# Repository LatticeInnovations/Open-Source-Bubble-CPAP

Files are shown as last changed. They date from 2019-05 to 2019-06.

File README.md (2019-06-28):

# Open-Source-Bubble-CPAP
This is an open source Bubble CPAP project
# This document is the chronological archive of the open bubble CPAP Design. It shows the working principle of the CPAP system

> ## [Iteration 1:](https://github.com/LatticeInnovations/Open-Source-Bubble-CPAP/tree/master/01.%20Base%20Design/Iteration%201) 

>> This is the first proposed design. It includes industrial grade as well as readily available off-the-shelf materials. 

>>[It consists of the basic fundamental parts of the system. I.e.](https://github.com/LatticeInnovations/Open-Source-Bubble-CPAP/tree/master/03.%20Materials%20and%20testing/iteration%201/BOM-rev01) 

>> - Air compressor
>> - Flow meter
>> - Humidifier
>> - PEEP bottle
>> - Nasal prong

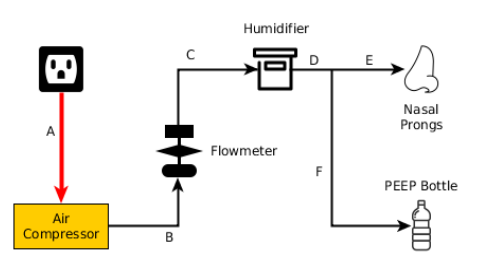
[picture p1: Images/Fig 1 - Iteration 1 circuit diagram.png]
Fig 1: Iteration 1 breathing circuit
>>> 

> ## [Iteration 2: ](https://github.com/LatticeInnovations/Open-Source-Bubble-CPAP/tree/master/01.%20Base%20Design/Iteration%202) 

>> Tests, observations and changes:

>> - Air compressor, alternative enclosure and hardware selection.
>> - [Breathing circuit pressure validation:](https://github.com/LatticeInnovations/Open-Source-Bubble-CPAP/blob/master/03.%20Materials%20and%20testing/iteration%202/Bubble%20VS%20Surface%20Humidifier%20Data/(S.H%20vs%20B.H)%201-of-2%20PEEP%20pressure%20validation%2026-06-2018.pdf) Relation between PEEP submersion depth (cm), Flow rate(Lpm) and pressure (manometer reading)
>> - Pressure deviations between bubbling & non-bubbling humidifiers.
>> - Water filling and submersion depth control.

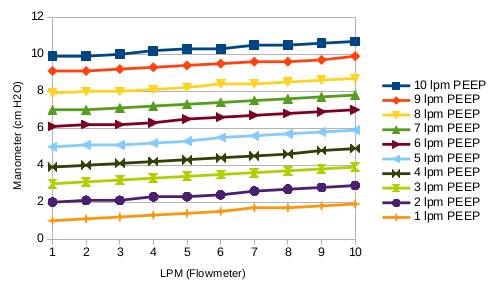
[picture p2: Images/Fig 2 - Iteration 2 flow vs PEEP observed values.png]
Figure 2: Iteration 2 - Flow vs PEEP observed values
>>> 

>> ### [Iteration 2.0](https://github.com/LatticeInnovations/Open-Source-Bubble-CPAP/tree/master/03.%20Materials%20and%20testing/iteration%202/iteration%202.0) 

>>> Gas detection (NH4, CO, CO2, Propane etc.) to identify the reason of smell inside the breathing circuit. 
>>> Effect on humidity with variable surface area inside the humidifier to control humidification.

>> ### [Iteration 2.1](https://github.com/LatticeInnovations/Open-Source-Bubble-CPAP/tree/master/03.%20Materials%20and%20testing/iteration%202/iteration%202.1) 

>>> Breathing circuit leakage detection technique and results

>> ### [Iteration 2.2](https://github.com/LatticeInnovations/Open-Source-Bubble-CPAP/tree/master/03.%20Materials%20and%20testing/iteration%202/iteration%202.2) 

>>> Load testing for 3 days & observations on stability of the in-circuit humidification irrespective of ambient temperature & humidity >>> change.

> ## [Iteration 3:](https://github.com/LatticeInnovations/Open-Source-Bubble-CPAP/tree/master/03.%20Materials%20and%20testing/iteration%203) 

>> - Comparison with Pumani and experiments on rebreathing of CO2 in Open bubble CPAP.
>> - Humidifier water filling mechanism with ball valve.
>> - Load testing with the new humidifier setup, continuous run for more than 8 hours
>> - Comparison between looped vs unidirectional (separate inspiratory & expiratory limb) nasal prongs usage

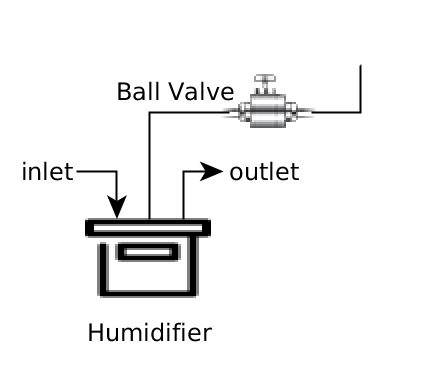
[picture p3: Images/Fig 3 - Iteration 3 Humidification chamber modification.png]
Figure 3: Iteration 3 - Humidification chamber modification
>>> 

> ## [Iteration 4:](https://github.com/LatticeInnovations/Open-Source-Bubble-CPAP/tree/master/03.%20Materials%20and%20testing/iteration%204) 

>> - Humidifier selection revised. Medical grade commonly available bottle shaped humidifiers. 
>> - Alternate silicone tubing for the breathing circuit. (ID-8mm, OD-12 mm)
>> - It has advantage of compatibility with a wide range of tube connectors.
>> - Oxygen blending feature addition in CPAP.
>> - 3-Flow-Meter method in contrast with existing pumani 2 FM design.
>> - Oxygen cylinder valve comparison and operating pressure levels selection.

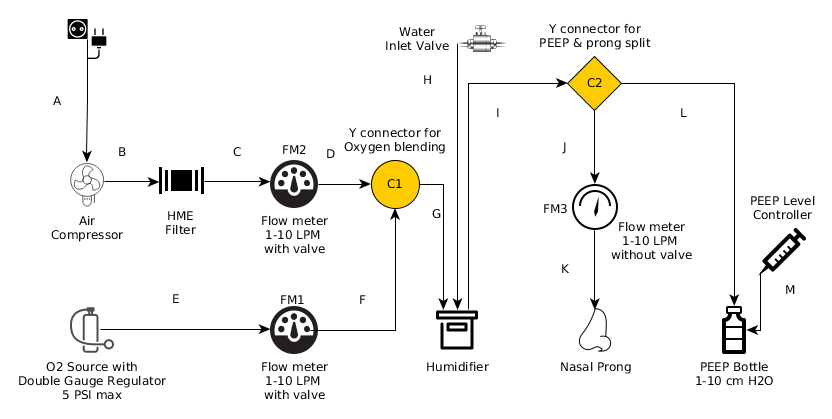
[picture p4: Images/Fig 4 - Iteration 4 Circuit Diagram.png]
Figure 4: Iteration 4 - Iteration 4 - Breathing Circuit
>>> 
***
## Development of OpenSource and affordable bubble CPAP system for neonatal respiratory care

.
#### Introduction:

Preterm infants commonly suffer from a respiratory/breathing disorder called neonatal respiratory distress syndrome (RDS) as their lungs are not yet fully developed. The disease is mainly caused by a lack of a slippery substance in the lungs called surfactant that helps the lungs fill with air and keeps the air sacs from deflating. The surfactant is present when the lungs are fully developed. Neonates suffering from RDS often need breathing support until their lungs start making enough surfactant. 

Continuous positive airway pressure (CPAP) as a therapy for respiratory distress syndrome, is the application of positive pressure to the airways of spontaneously breathing neonates throughout their respiratory cycle.

#### Aim:

Conventional CPAP is very expensive and hence not affordable in resource-constrained settings. Locally available hardware such as low-cost plastic bottles, tubing, connectors and air pumps are used in this design to develop an affordable and modular Bubble CPAP device. With the modular CPAP approach, we intend to locally train more people on how to develop and troubleshoot CPAP devices. 

#### Purpose of usage:
- Maintaining both breathing parameters i.e. the volume and the pressure of the inhaled gas to the lungs in order to prevent lung collapse among RDS affected neonates/patients.
- To make sure that the prescribed level of oxygen is supplied to the patient through the air/O2 mixture so that it can take part in the gas exchange process in the alveoli.
- Helping the patient breath by reducing the work of breathing.

### How to use this document: 

This opensource DIY design of this bubble CPAP is module driven. The entire design is divided into three segments: 

**1. [Base Design](https://github.com/biplabro/Open-Source-Bubble-CPAP/tree/master/01.%20Base%20Design) :**
This is the bare minimum design of the Bubble CPAP system and it represents the updated design guidelines of the latest design iterations.

**2. [Optional Add-ons](https://github.com/biplabro/Open-Source-Bubble-CPAP/tree/master/02.%20Optional%20Add-ons) :**
This section of the document includes all the additional hardware 

**3. [Material Specifications & Testing Protocols](https://github.com/biplabro/Open-Source-Bubble-CPAP/tree/master/03.%20Materials%20and%20testing) :**
In this section, hardware materials, test procedures and outputs are discussed. 

**The idea of the development process is:**
- To build a working CPAP device using the most commonly used & readily available resources.
- To shrink the base design while retaining the robustness, reliability and functionality of the system so that it can be used as a standalone bare minimum design.
- To include more resources, features and test cases in the Optional Add-ons & Testing protocols segments so that it can be further developed with different design approaches.

#### Features and specifications:

* Flow rate: 1 to 10 lpm
* PEEP: equivalent to 1 to 10 cm of water column
* Power input: 220v, 50Hz (inpun is air compressor dependant and entirely flexible)
* HME filtration (optional) for particulate free clean air.
* Both valve regulated or disposable humidifier can be used for easy access
* 3-flowmeter design for better air-oxygen blending and control of the total flow. 
* Can be built from scratch & easily accessible off-the-shelf components based desig.
* Max pressure for O2 cylinder interface: 5 PSI

**How to build:**

The [“01. Base Design”](https://github.com/biplabro/Open-Source-Bubble-CPAP/tree/master/01.%20Base%20Design)  folder includes all the building iterations. [“Iteration 5”](https://github.com/biplabro/Open-Source-Bubble-CPAP/tree/master/01.%20Base%20Design/Iteration%205)  (or the largest number) sub-folder includes the latest build instructions with pictures. 

Size and outlook of the built devices across the globe may differ depending on the availability of the components/ alternative components.

[**Base Design:**](https://github.com/LatticeInnovations/Open-Source-Bubble-CPAP/tree/master/01.%20Base%20Design) 

1. Base device is intended to be treated as a self sufficient working model of the bubble CPAP system. 

2. BOM, available datasheets etc. are included in the “03. Material and testing” folder. We have to keep in mind that the generic components like silicone tubing, HME filters etc. can come from different local and global manufacturers. Every iteration done by the users must include the actual images to help others source the desired item.

3. The basic working principle of respiratory support system like bubble CPAP is to provide the patient with air and gas supply with controlled Volume & Pressure to prevent their lung from collapsing. The flow-meters deployed in the breathing circuit takes care of the volume of the exhausted air/oxygen mixture from the device and the water submersion leven inside the PEEP determines the exerted pressure level to the patient’s lungs. 

4. In the last iteration air. Oxygen is blended through a Y-connector piece with regulated flow and pressure. A table of O2/Air mixture concentration is included in the “03. Material and testing” folder for reference. 
 5. Every tube-connector junction is to be fixed properly to assure no leakage within the breathing circuit.
 
[**Optional Add-ons:**](https://github.com/LatticeInnovations/Open-Source-Bubble-CPAP/tree/master/02.%20Optional%20Add-ons)

1. Optional add-ons can or cannot be implemented with the base design. It entirely depends on the access & availability of the additional components. 

2. HME filters, Valve regulated water filling technique etc. should be considered as extra that does not have a significant direct impact on the usability of the base device. 

3. Users are encouraged to include additional hardware to their respective system to make it more robust & reliable.

[**Materials & Testing Protocols:**](https://github.com/LatticeInnovations/Open-Source-Bubble-CPAP/tree/master/03.%20Materials%20and%20testing) 

This folder includes the following :
- all the testing protocol and experiment data, 
- Software codes required for conducting the experiments. 
- Bill of materials and observations on 
	    1. O2 concentrator
   	2. Flow meter etc
  	3. comparison on different nasal prongs
  	4. Filters
 	5. Pressure levels for interfacing external oxygen cylnder
 	
 Enlisting all the tests conducted from phase 1 to phase 3 and how the development is iterated based on the test results

**Other:**
Tubing of the breathing circuit is preferred to be of same internal dia, it will assure more accurate readings with the flow-meter.

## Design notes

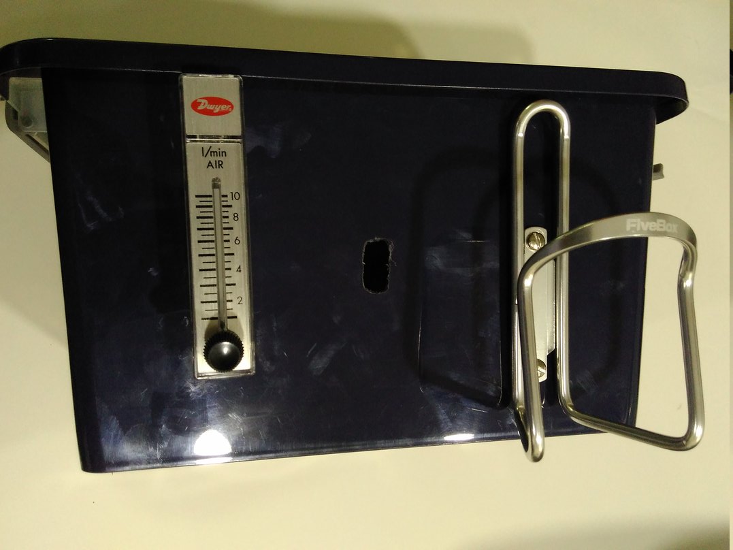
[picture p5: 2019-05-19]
01. Base Design/Iteration 1/Design files/Images_rev01/rev01-19.jpg

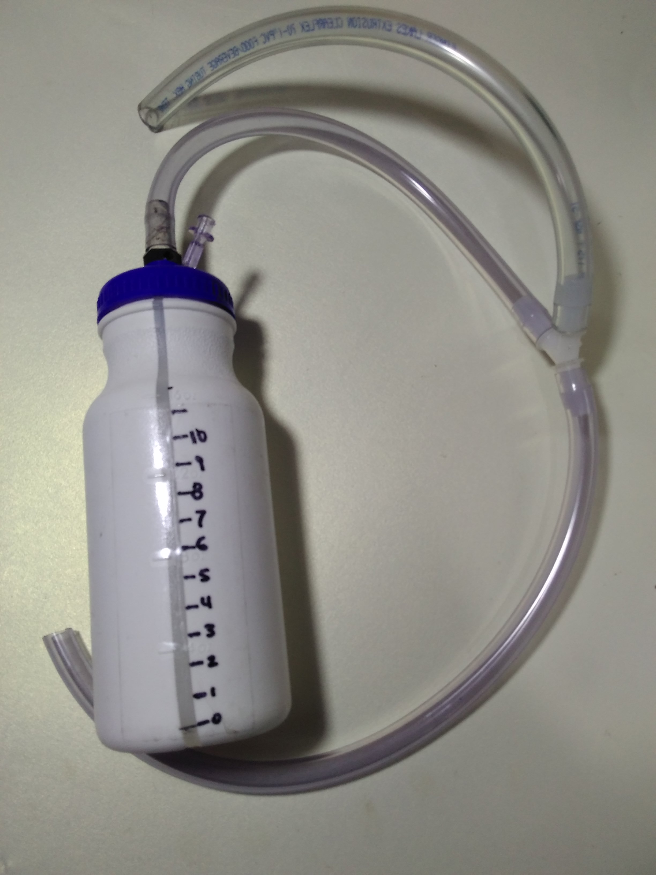
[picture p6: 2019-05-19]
01. Base Design/Iteration 1/Design files/Images_rev02___rev03/rev02-23.jpg

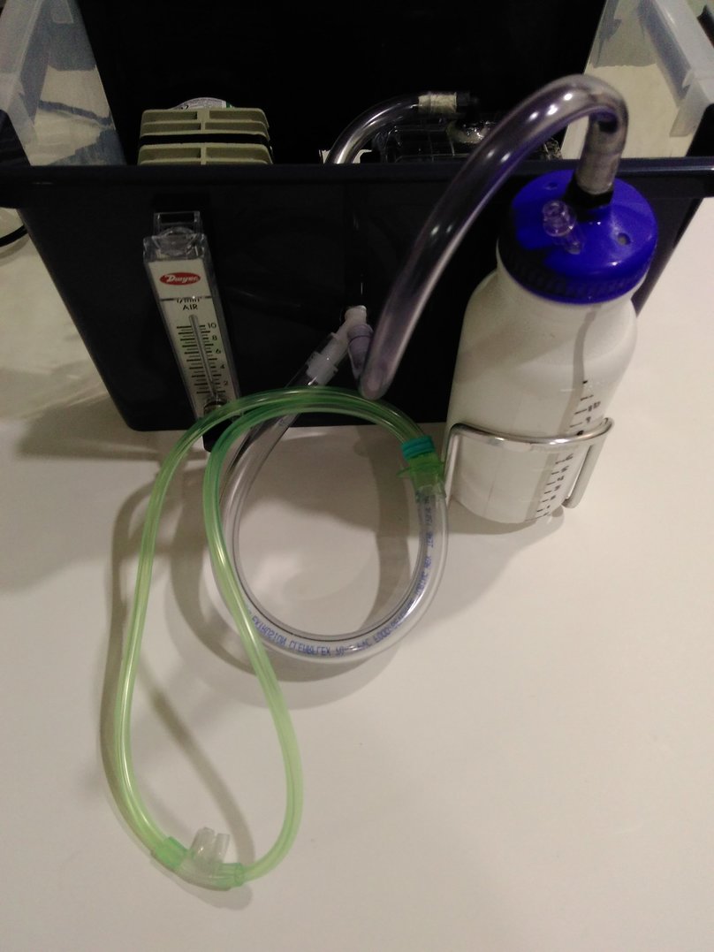
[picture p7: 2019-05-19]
01. Base Design/Iteration 1/Design files/Images_rev01/rev01-27.jpg

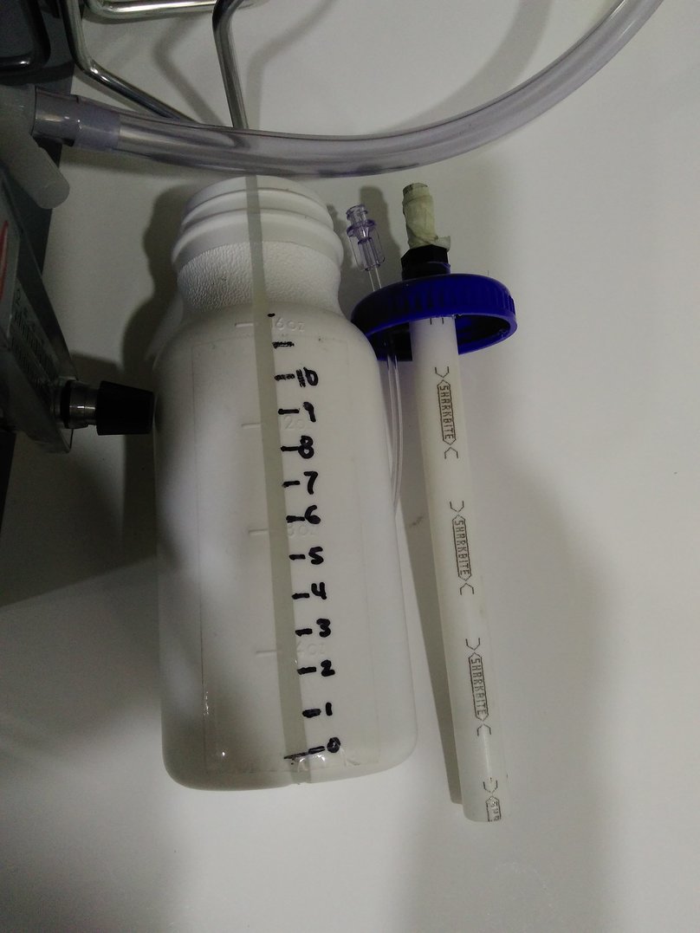
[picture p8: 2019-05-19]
01. Base Design/Iteration 1/Design files/Images_rev01/rev01-25.jpg

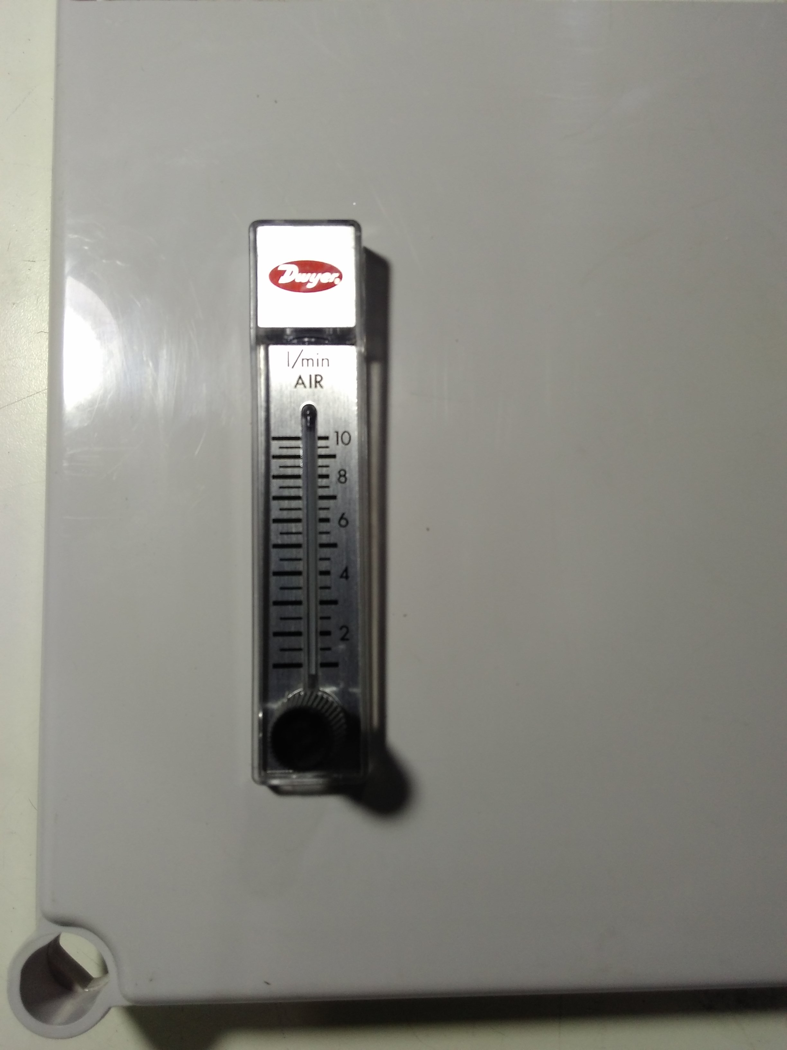
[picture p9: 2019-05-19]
01. Base Design/Iteration 1/Design files/Images_rev02___rev03/rev02-17.jpg

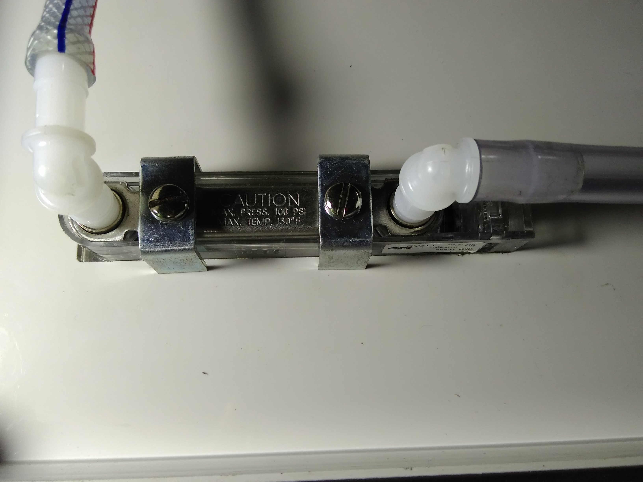
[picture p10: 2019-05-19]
01. Base Design/Iteration 1/Design files/Images_rev02___rev03/rev02-20.jpg

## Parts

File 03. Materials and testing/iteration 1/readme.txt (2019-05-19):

Readme: Low-cost Bubble CPAP device development. This folder contains all the test protocol, results, data & plots.

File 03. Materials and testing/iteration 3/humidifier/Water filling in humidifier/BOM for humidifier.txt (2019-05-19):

1. Forged ball valve 1/2" 
2. Nozzle for ball valve 1/2" to 3/8"
3. Tube fasteners 3/4"
4. Teflon tape
5. U clamp 1" dia, 3/4" width
6. Funnel for pouring water (optional)

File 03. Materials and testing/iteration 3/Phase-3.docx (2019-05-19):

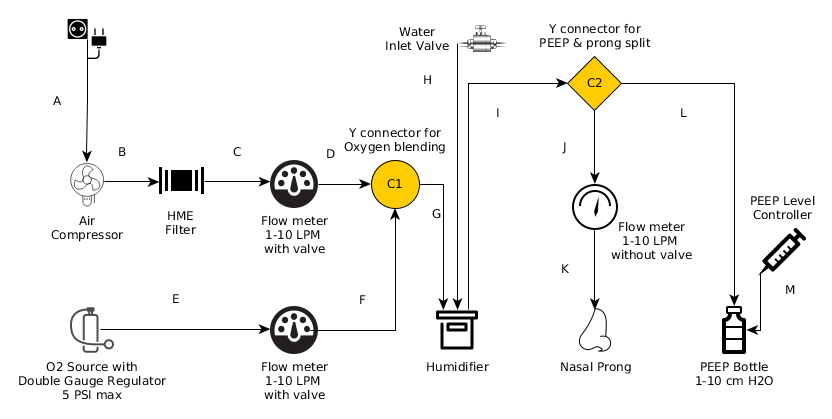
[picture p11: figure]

Water Inlet Valve

Y connector for PEEP & prong split

C2

Y connector for Oxygen blending

сі

PEEP Level Controller

Air Compressor

HME Filter

Flow meter

1-10 LPM with valve

Flow meter

1-10 LPM without valve

>6

Humidifier

Nasal Prong

02 Source with Double Gauge Regulator

5 PSI max

Flow meter

1-10 LPM with valve

PEEP Bottle 1-10 cm H2O

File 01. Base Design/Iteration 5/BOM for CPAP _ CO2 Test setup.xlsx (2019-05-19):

 | All materials are referenced to the attached system schematic diagram
 |  |  |  |  |  |  | Legends:
 |  |  |  |  |  |  | Optional Item
Sl. No. | Component Type | Count | As shown in Diagram | Vendor | Manufacturer Part No. | Description | Datasheet | product link | link for purchase
1 | Air compressor | 1 no. | Air compressor | Amazon India | ACO-308 | Hailea Air Compressor ACO-308, 22W. 220V/50Hz; 45LpM | http://www.aeroponic.gr/en/eshop/hailea-aco-308-detail.pdf?tmpl=component | http://www.hailea.com/e-hailea/product3/ACO-308.htm | http://www.amazon.in/HAILEA-ACO-308-Hailea-Air-Compressor/dp/B0083UFKDG
2 | L connector for Flowmeter | 4 nos. | C-FM2-D, E-FM1-F, M-FM3-N | McMASTER-CAR | 2808K121 | Polyethylene Barbed Tube Fitting 90 Degree for 3/8“ Elbow Tube | https://www.mcmaster.com/#2808k121/=189an7w | https://www.mcmaster.com/#2808k121/=189an7w | https://www.mcmaster.com/#2808k121/=189an7w
3 | HME filter Disk type | 1 no. |  |  |  |  |  | http://mederen.com/uploads/catalogue/respiratory_and_anestesia/heats/thumbnail/h2-f1000x1000.jpg | https://www.larsmedicare.com/hme-filter/
4 | Flow meter 1-10 LPM | 3 nos. | FM1, FM2, FM3 | Amazon | homyl | Homyl 1-10LPM Tube Type Oxygen Flow Meter Flowmeter Regulator With Valve,Measuring And Controlling Air |  | https://www.amazon.in/gp/product/B07HSKD591/ref=oh_aui_search_detailpage?ie=UTF8&psc=1
5 | End cap for fitting HME filter with tube | 2 nos.
6 | alternative HME filter (no extra end cap required, replacement for tem no. 5 & 6) | 1 no. |  |  |  |  |  | https://scientificfilters.com/store/filtration-devices-syringe-filter-rezist-10463607
7 | Straight connector with threading | 3 nos. | G-Humidifier-H-I | McMASTER-CAR | 2429k16 | Plastic Barbed Tube Fitting for Air and Water | https://www.mcmaster.com/2429k16 | https://www.mcmaster.com/2429k16 | https://www.mcmaster.com/2429k16
8 | Tubing for breathing circuit | 7 mtr. | A,B,C,D,E,F,G,H,I,J,K,L,M,N | Generic |  | Tube ID: 8mm, OD: 12mm, soft silicone, Lab equipment grade, autoclavable |  | https://www.alibaba.com/showroom/silicone-tube-for-laboratory.html
9 | Humidifier chamber | 1 no. | Humidifier | Roxx |  | small Plastic Waterproof Airtight Case |  | https://www.amazon.in/gp/product/B007PDU6IQ/ref=oh_aui_search_detailpage?ie=UTF8&psc=1
10 | alternative disposable humidifier chamber | 1 no. |  | Generic |  | Medical grade humidifier |  | https://www.4mdmedical.com/disposable-humidifier-6-psi.html
11 | Y connector (1 for CO2 testing) | 2 +1 nos. | C1, C2, C3 | McMASTER-CAR | 2808K131 | Plastic Wye Connector, for 3/8" Tube ID | https://www.mcmaster.com/#2808k131/=189hu45 | https://www.mcmaster.com/#2808k131/=189hu45 | https://www.mcmaster.com/#2808k131/=189hu45
12 | Ram cannula | 1 no. | Nasal Prong | http://pro-med.cn | P2001001, P2001002, P2001003, P2001004 | Nasal Oxygen Cannula |  | http://pro-med.cn/PRODUCTS/RespiratoryRanges/340484.shtml | http://pro-med.cn/PRODUCTS/RespiratoryRanges/340484.shtml
13 | PEEP bottle | 1 no. | PEEP bottle | Quechua |  |  |  | http://www.amazon.in/Quechua-Hiking-Bottle-Cutlery-Yellow/dp/B00HZETOS8 | http://www.amazon.in/Quechua-Hiking-Bottle-Cutlery-Yellow/dp/B00HZETOS8
14 | Adjustable Bottle holder | 1 no. | PEEP bottle | Generic |  | Bottle Carrier Bracket |  | http://www.amazon.in/Arrival-Adjustable-Plastic-Cycling-Accessories/dp/B01MG1YRLG | http://www.amazon.in/Arrival-Adjustable-Plastic-Cycling-Accessories/dp/B01MG1YRLG
15 | PVC tube inside PEEP Bottle | 6" | PEEP bottle | Generic |  | OD: 16mm ; ID: 12mm
16 | Sytinge for PEEP level control | 1 no. | PEEP level controller |  |  |  |  |  | https://www.amazon.in/SaiDeng-Reusable-Syringes-Cleaning-Measuring/dp/B07Q12KHPD?s=kitchen
17 | CPAP enclosure | 1 no. |  | Rolec India | BC-AGS -283818 | Enclosure for CPAP device |  | http://www.rolecenclosures.in/
18 | Forged ball valve 1/2" | 1 no. | Water inlet valve |  |  |  |  | images attached in the folder
19 | Nozzle for ball valve 1/2" to 3/8" | 2 nos. | Water inlet valve
20 | Tube fasteners 3/4" | 2 nos. | Water inlet valve
21 | Teflon tape | 1 nos. | Water inlet valve
22 | U clamp 1" dia, 3/4" width | 2 nos.
23 | Funnel for pouring water (optional) | 1 nos.
24 | Oxygen cylinder regulator | 1 nos. | O2 Source Regulator |  |  | Dual gauge single stage valve regulator |  | https://www.amazon.in/Bloomerang-Welding-Victor-Cutting-Regulator/dp/B07JM6RMK4
25 | CO2 testing enclosure | 1 No. |  |  |  | Bottles similar to this |  | https://www.amazon.in/Cello-Unbreakable-Plastic-Bottle-Litre/dp/B01BYBTZJA?s=kitchen
26 | MQ-135 CO2 sensor | 2 nos. | Sensor |  |  |  | https://www.olimex.com/Products/Components/Sensors/Gas/SNS-MQ135/resources/SNS-MQ135.pdf | https://www.amazon.in/REES52-Arduino-Compatible-Sensor-Methane/dp/B018GW70G0?s=gateway
27 | Arduino UNO with USB cable | 1 no. | Data logging Module |  |  |  | https://www.farnell.com/datasheets/1682209.pdf | https://www.amazon.in/Uno-ATmega328P-Compatible-ATMEGA16U2-Arduino/dp/B015C7SC5U?s=gateway

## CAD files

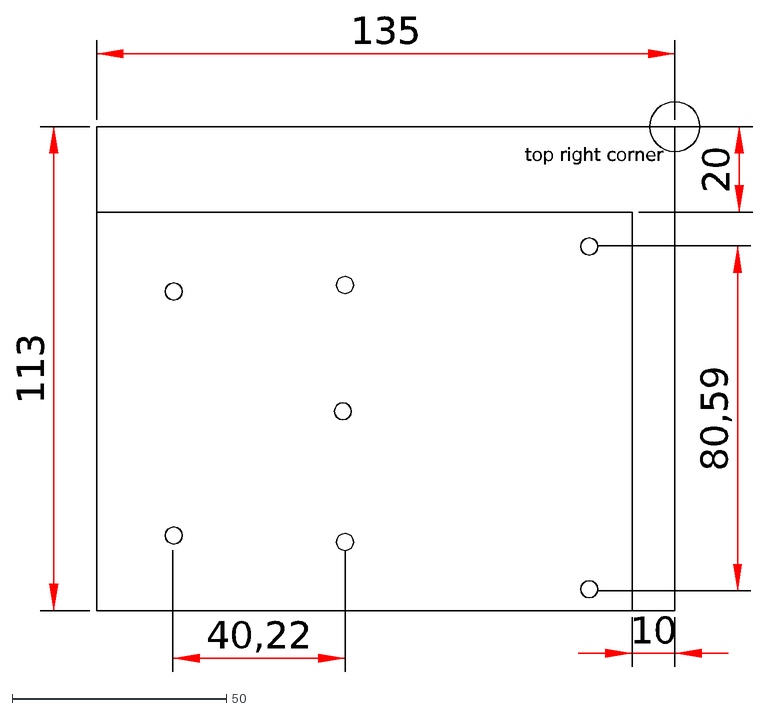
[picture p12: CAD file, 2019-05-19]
01. Base Design/Iteration 1/Design files/CPAP_Baseplate_file.dxf
10
20
113
135
top right corner
40,22
80,59

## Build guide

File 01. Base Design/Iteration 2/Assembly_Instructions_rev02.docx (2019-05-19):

Assembly instruction for CPAP device

Step 1.1 Prepare the cut outs in the main enclosure

Step | Instruction | Image

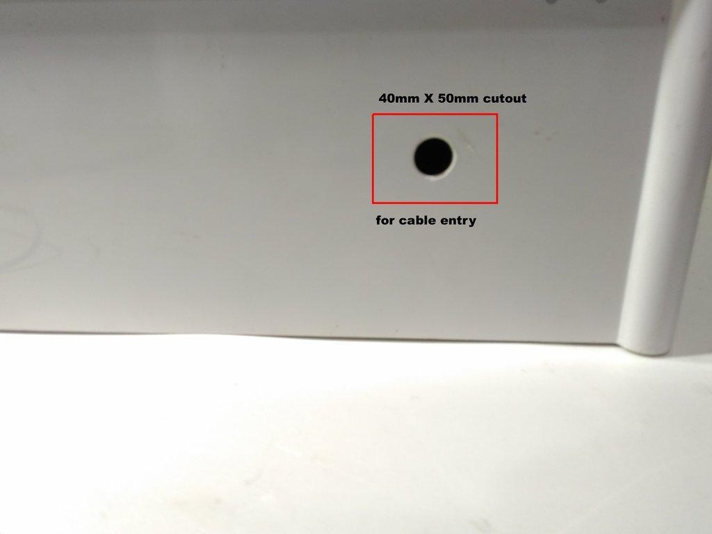
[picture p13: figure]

1.0 | Make a 40mm X 50mm clearance for cable inlet at any of the side walls of the enclosure. | Fig.0

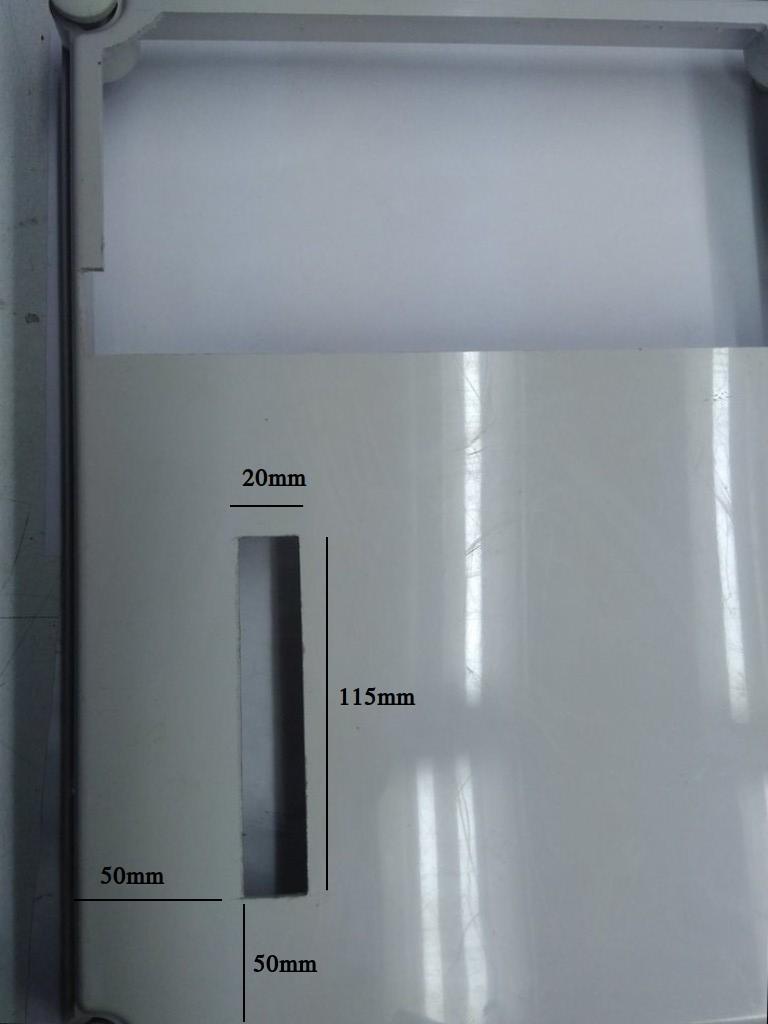
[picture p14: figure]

| Note the location of the flowmeter installation cavity. | Fig.1

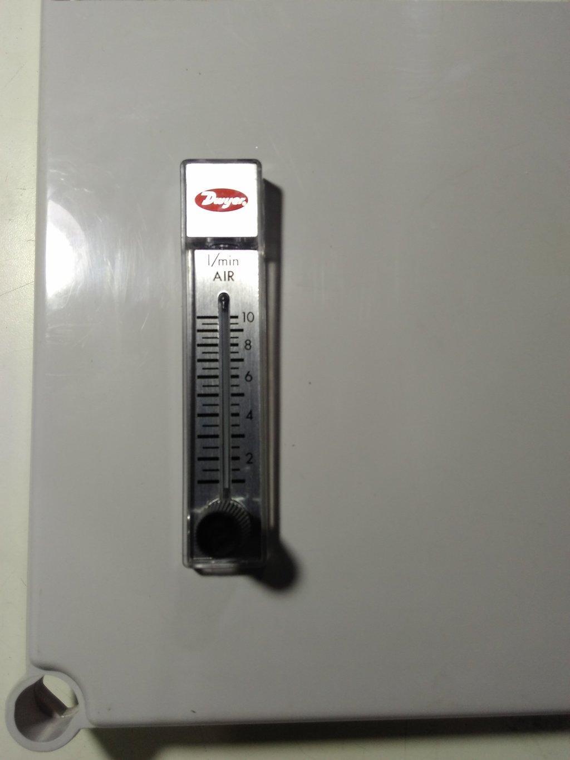
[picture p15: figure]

1.2 | Place it as shown | Fig.2

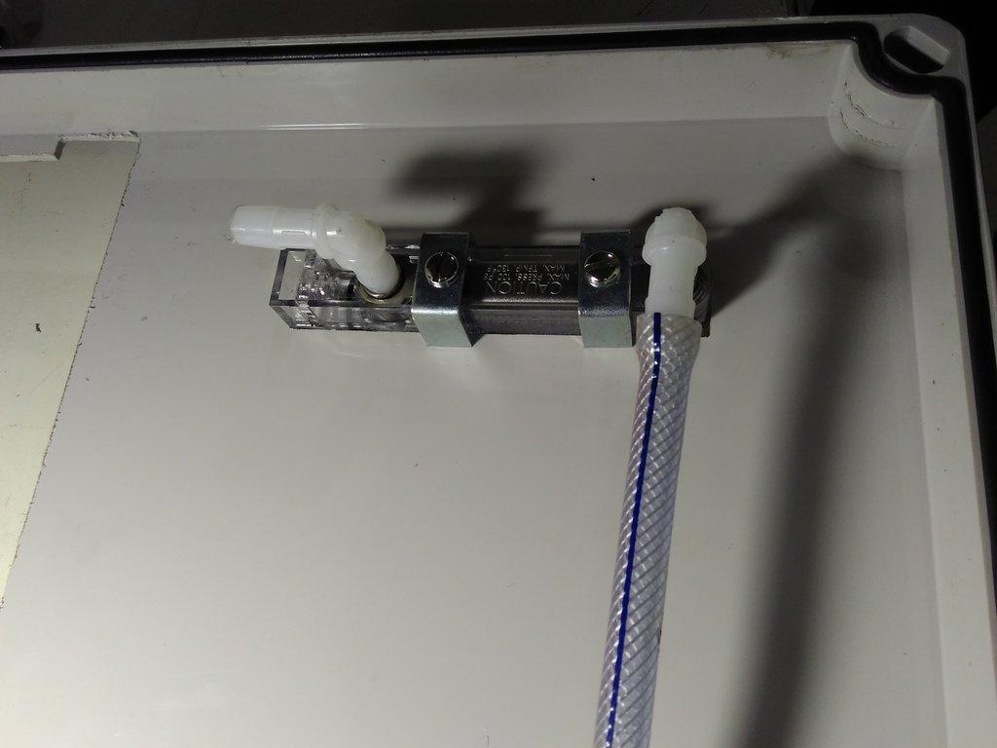
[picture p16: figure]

1.3 | Fix the screws to keep the flowmeter in place. | Fig.3

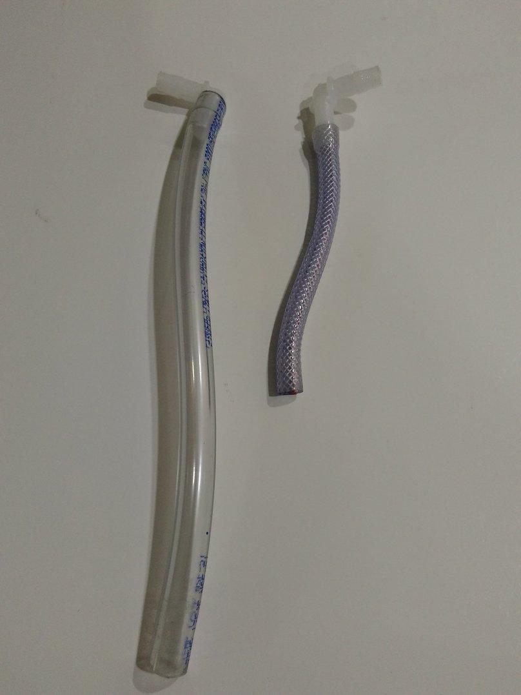
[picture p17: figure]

1.4 | Cut two PVC tubes of 250mm & 120mm length & connect the elbow connectors to the tubes as shown in the picture. | Fig.4

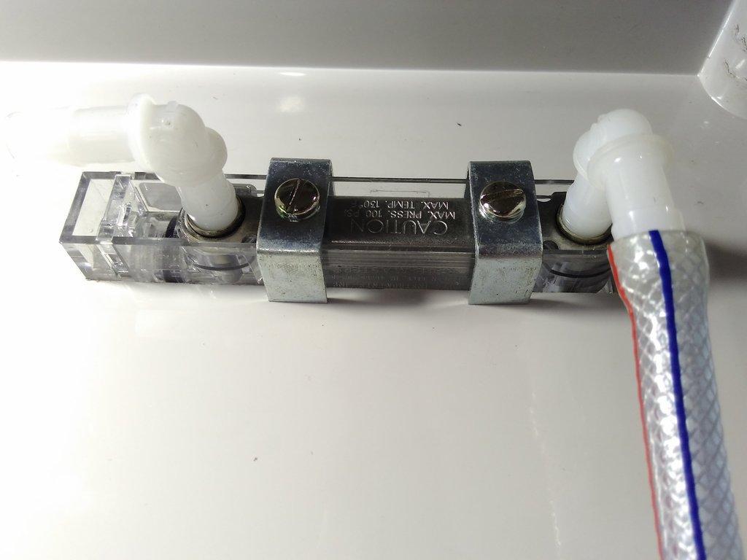
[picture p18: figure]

1.5 | Connect the tubes to the flowmeter. There are no threads built in to the plastic connectors, tighten the elbow connectors carefully & the metal threads will automatically cut the plastic & make an airtight threading. | Fig.5

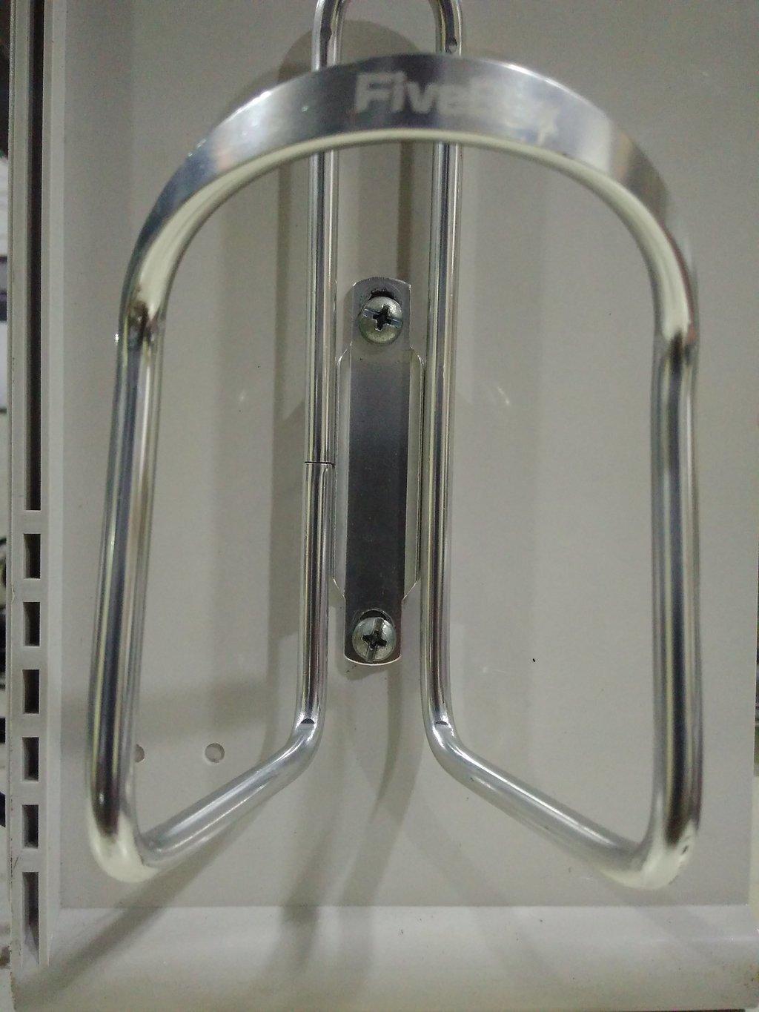
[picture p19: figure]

1.6 | Drill two holes of 5mm dia & 65mm apart and fix the bottle holder in that location. | Fig.6

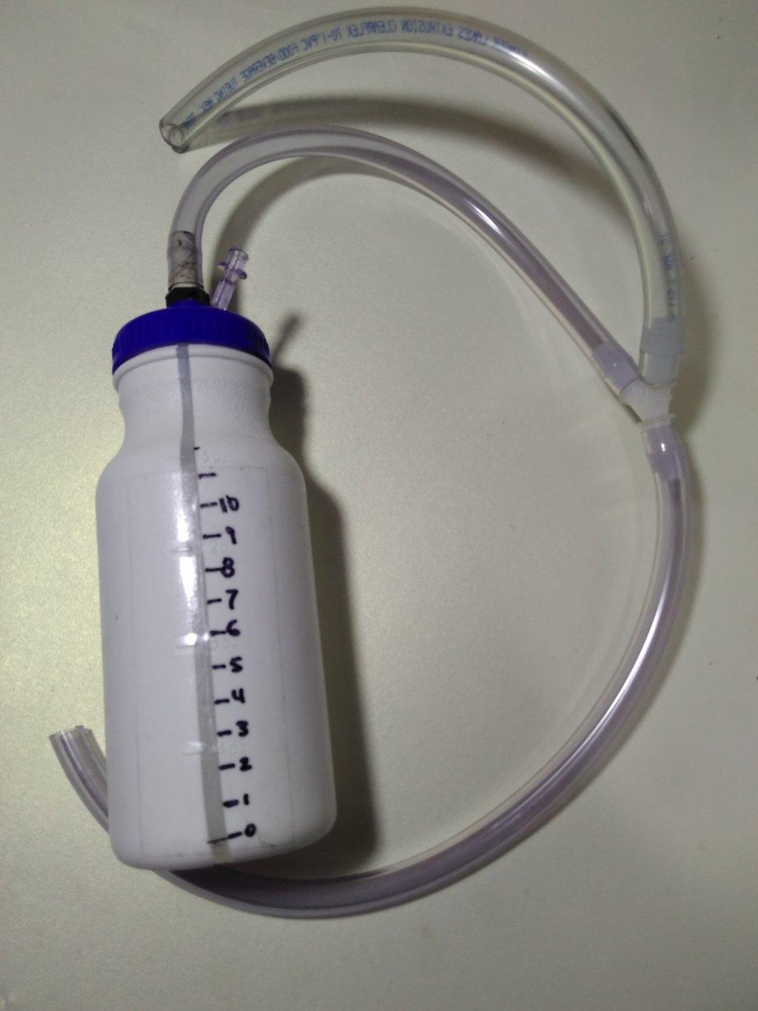
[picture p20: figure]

1.7 | Prepare the PEEP bottle assembly | Fig.7

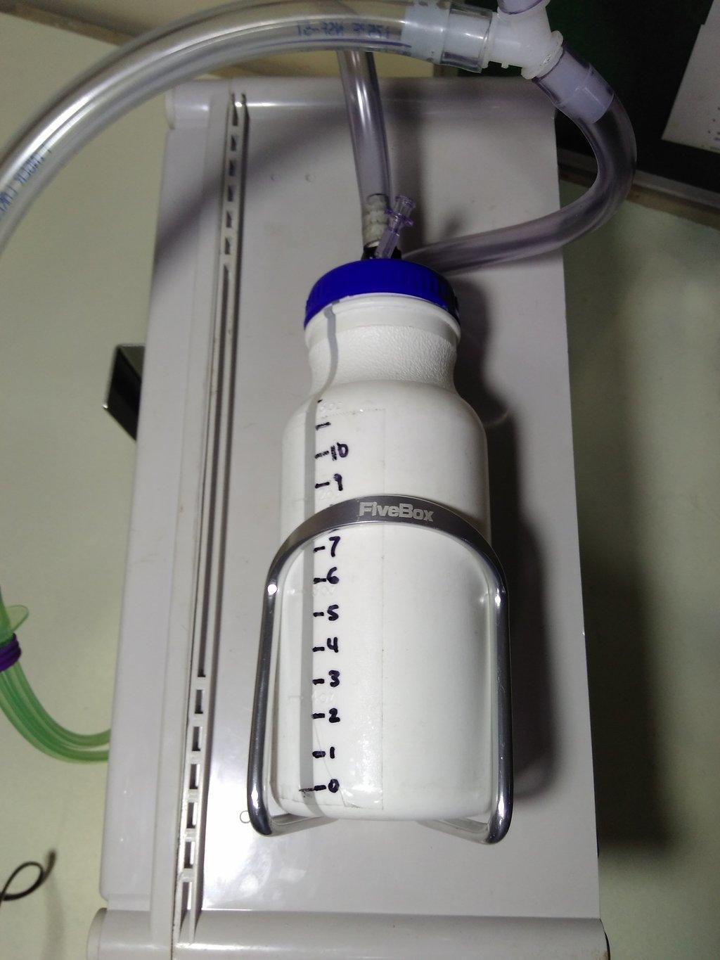
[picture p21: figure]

| PEEP bottle to be mounted as shown. | Fig.8

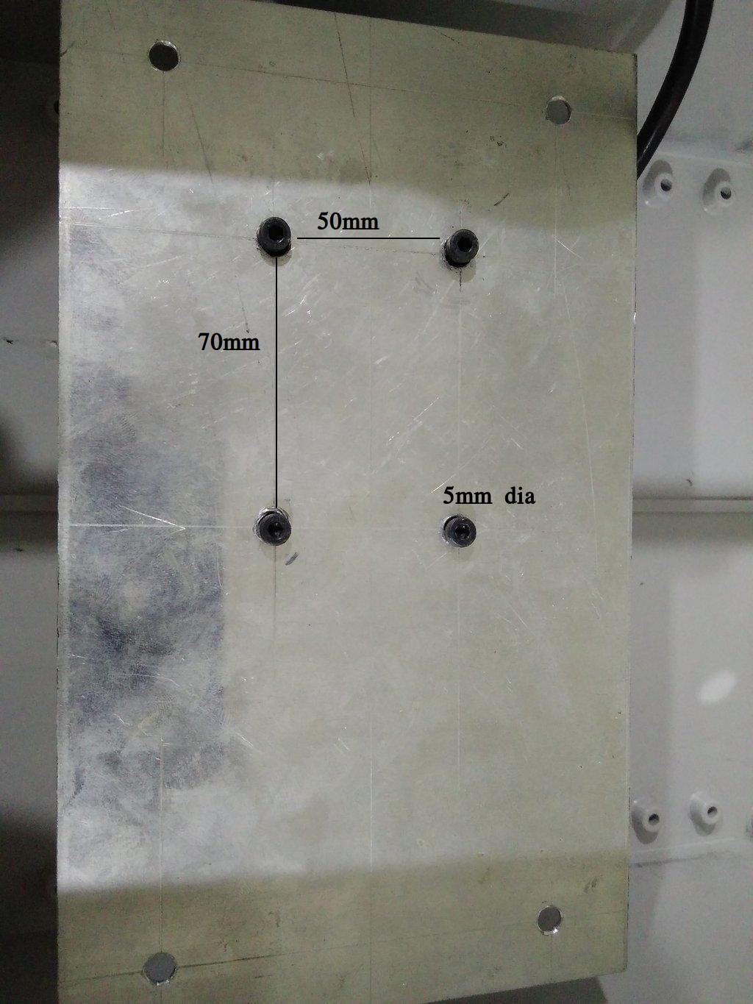
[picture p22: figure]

| Prepare the base-plate for compressor mounting. Placement of the holes may differ depending on their actual mounting arrangement | Fig.9

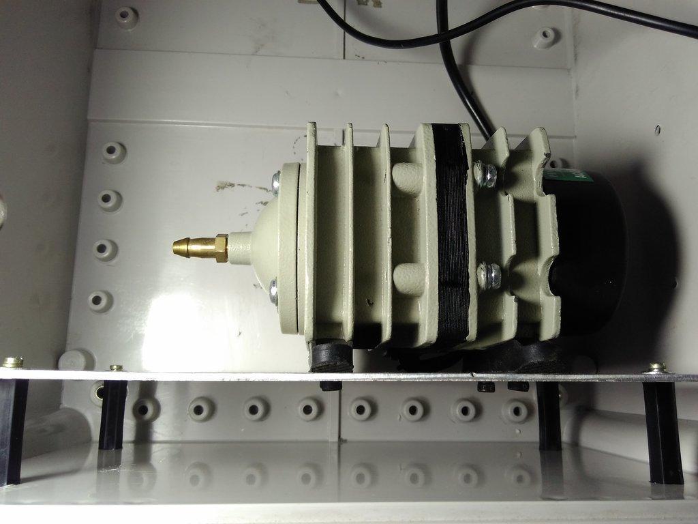
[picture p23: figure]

1.8 | Assemble the pump & place it in the mounting holes. Make 4 mounting holes for placing the baseplate inside the enclosure. Dimension: 190mm X 90mm | Fig.10

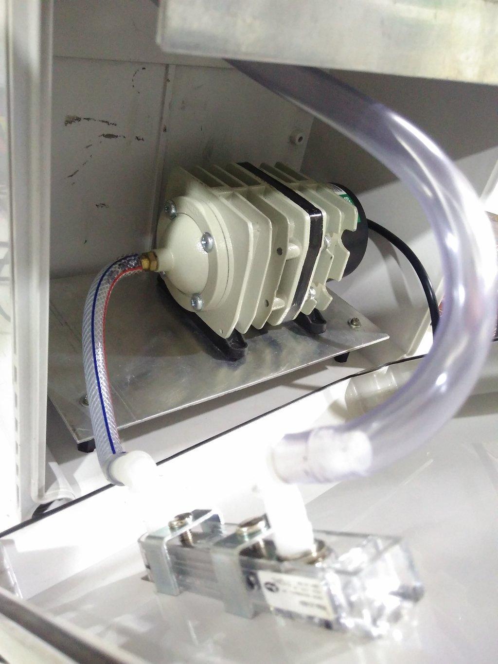
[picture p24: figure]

| Connect the compressor outlet to the flowmeter inlet as shown. The outlet of the flowmeter to be connected to the inlet of the humidifier. | Fig.11

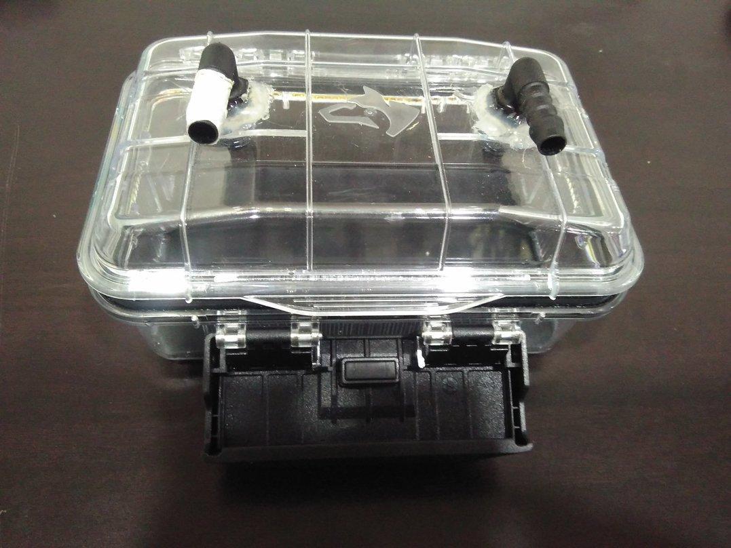
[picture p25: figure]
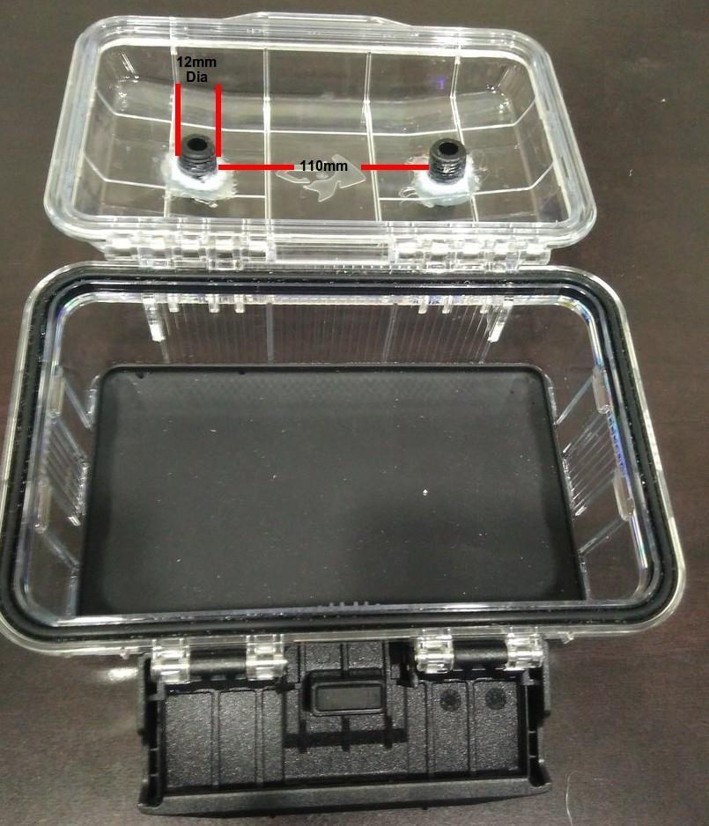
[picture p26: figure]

1.9 | Preparation of the Humidifier Drill two holes of 12mm dia & 110mm apart and place the threaded elbow connector as shown in the image. Some masking tape can be applied for achieving better grip & air-tightness. | Fig.12 Fig.13

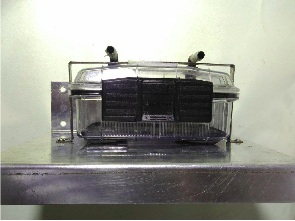
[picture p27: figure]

1.10 | Place the humidifier chamber in the appropriate place. | Fig.14

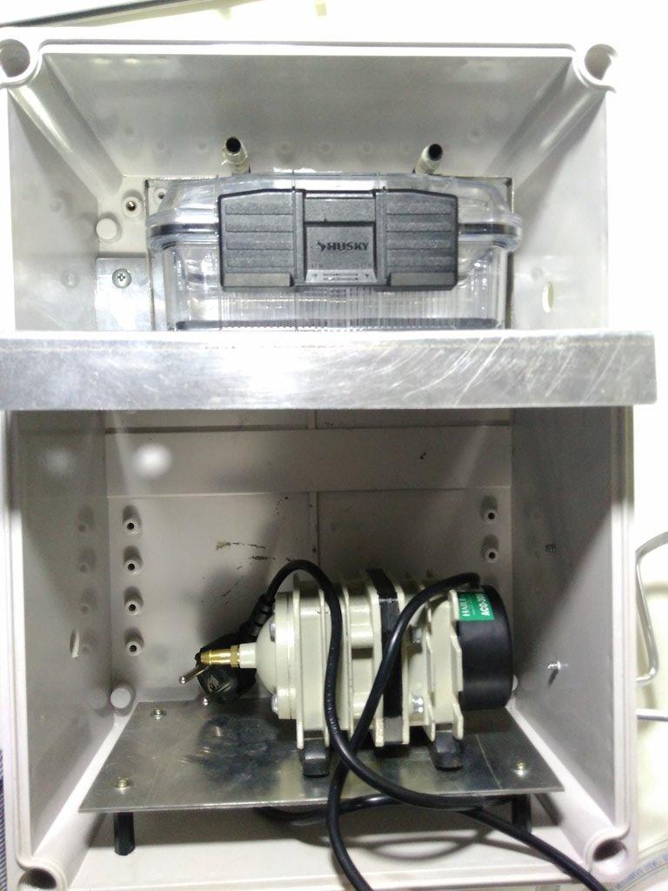
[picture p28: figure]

1.11 | The final placement of compressor & humidifier | Fig.15

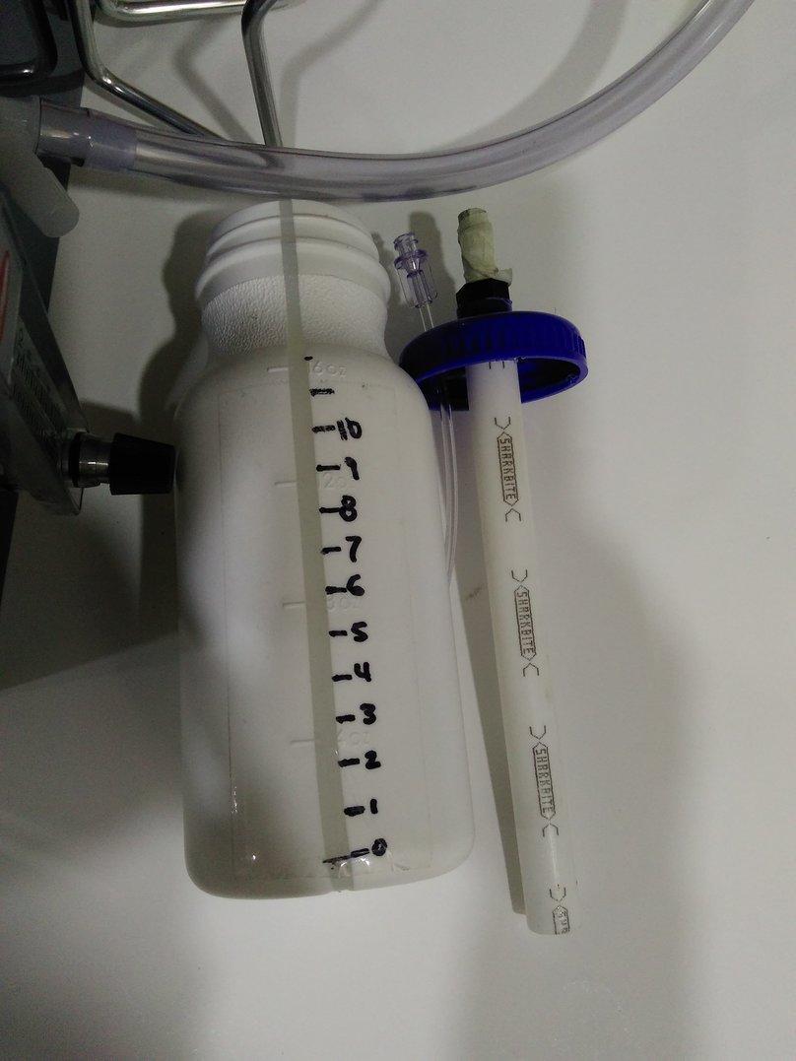
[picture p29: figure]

1.12 | Drill a hole of 12mm diameter at the center of the cap of the bottle & place the threaded connector & 180mm PVC pipe of 12mm internal diameter. Drill 4 holes of 5mm diameter at the cap of the bottle to insert luer lock tubing. This tube will be connected to a 60ml or 100ml syringe for adding or reducing water to the PEEP bottle. | Fig.16
1.13 | Cut a 115mm tube & place it in between the humidifier chamber outlet & Y connector. Connect the nasal cannula & tubing to the wye connector. | Fig.17

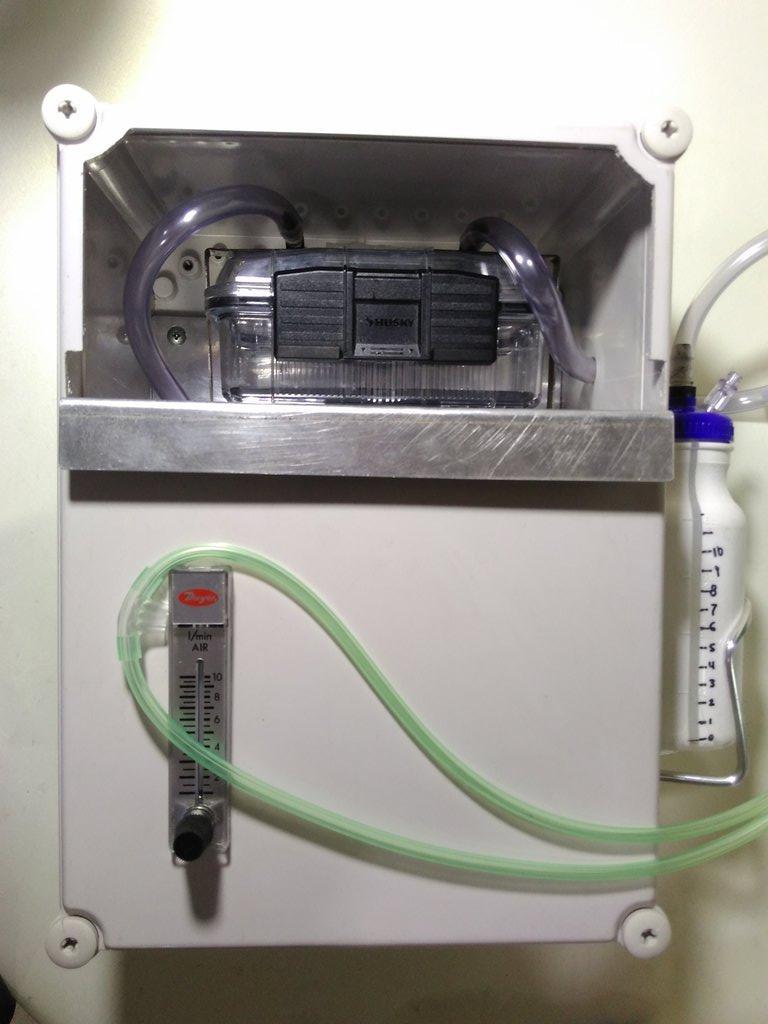
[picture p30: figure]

1.14 | Assembled bubble CPAP | Fig.18

For Internal use only Lattice Innovations FYVE S1 SOP Assembly Instructions Document No – LI/QM/SOP/AI/CPAP Version No. 02 New ___ _________ Revised ___________ Effective Date: Issuing Date: 17-07-201

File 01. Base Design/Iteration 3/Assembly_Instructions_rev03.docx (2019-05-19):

Assembly instruction for CPAP device

Step 1.1 Prepare the cut outs in the main enclosure

Step | Instruction | Image


1.0 | Make a 40mm X 50mm clearance for cable inlet at any of the side walls of the enclosure. | Fig.0


| Note the location of the flowmeter installation cavity. | Fig.1


1.2 | Place it as shown | Fig.2


1.3 | Fix the screws to keep the flowmeter in place. | Fig.3


1.4 | Cut two PVC tubes of 250mm & 120mm length & connect the elbow connectors to the tubes as shown in the picture. | Fig.4


1.5 | Connect the tubes to the flowmeter. There are no threads built in to the plastic connectors, tighten the elbow connectors carefully & the metal threads will automatically cut the plastic & make an airtight threading. | Fig.5


1.6 | Drill two holes of 5mm dia & 65mm apart and fix the bottle holder in that location. | Fig.6


1.7 | Prepare the PEEP bottle assembly | Fig.7


| PEEP bottle to be mounted as shown. | Fig.8


| Prepare the base-plate for compressor mounting. Placement of the holes may differ depending on their actual mounting arrangement | Fig.9


1.8 | Assemble the pump & place it in the mounting holes. Make 4 mounting holes for placing the baseplate inside the enclosure. Dimension: 190mm X 90mm | Fig.10


| Connect the compressor outlet to the flowmeter inlet as shown. The outlet of the flowmeter to be connected to the inlet of the humidifier. | Fig.11

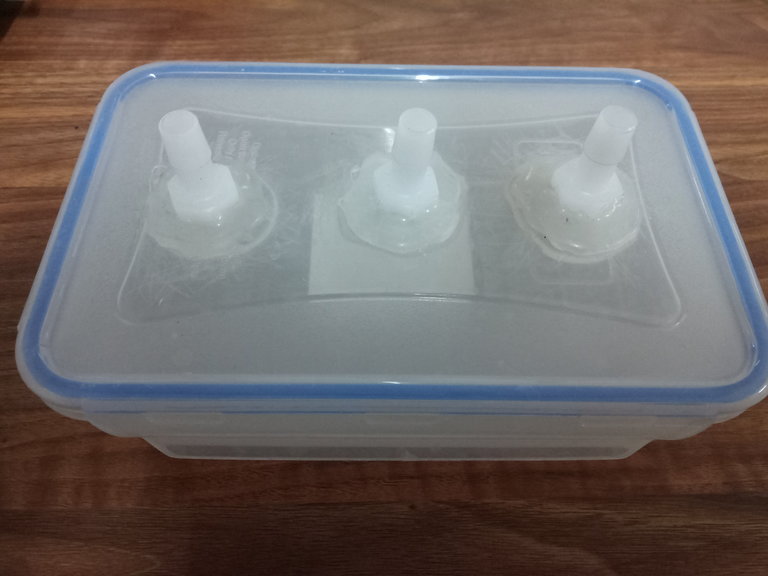
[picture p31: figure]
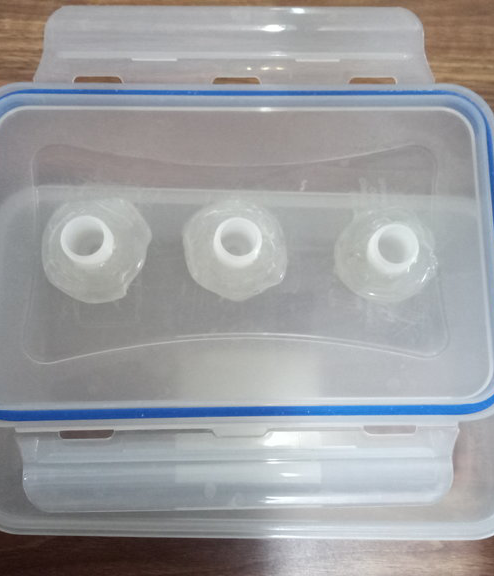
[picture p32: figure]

1.9 | Preparation of the Humidifier Drill three holes of 12mm dia & 50mm apart and place the threaded elbow connector as shown in the image. Inlet and outlet port of the humidifier & water filling connector. Some masking tape/ glue gun can be applied for achieving better grip & air-tightness. | Fig.12 Fig.13

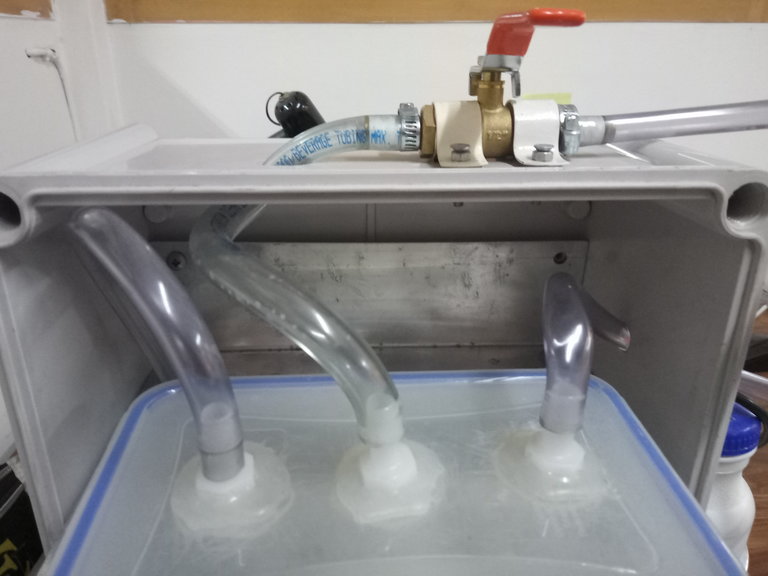
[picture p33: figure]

1.10 | A ball valve is set at the top of the system to fill water in the humidifier. Place the humidifier chamber in the appropriate place. | Fig.14

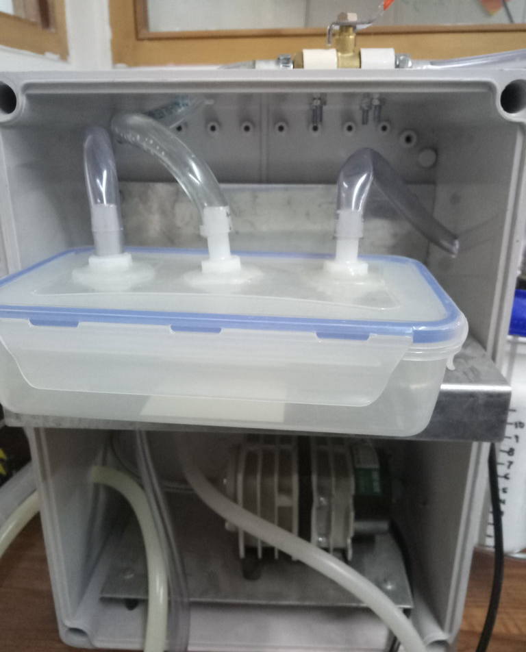
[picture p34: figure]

1.11 | The final placement of compressor & humidifier | Fig.15


1.12 | Drill a hole of 12mm diameter at the center of the cap of the bottle & place the threaded connector & 180mm PVC pipe of 12mm internal diameter. Drill 4 holes of 5mm diameter at the cap of the bottle to insert luer lock tubing. This tube will be connected to a 60ml or 100ml syringe for adding or reducing water to the PEEP bottle. | Fig.16
1.13 | Cut a 115mm tube & place it in between the humidifier chamber outlet & Y connector. Connect the nasal cannula & tubing to the wye connector. | Fig.17

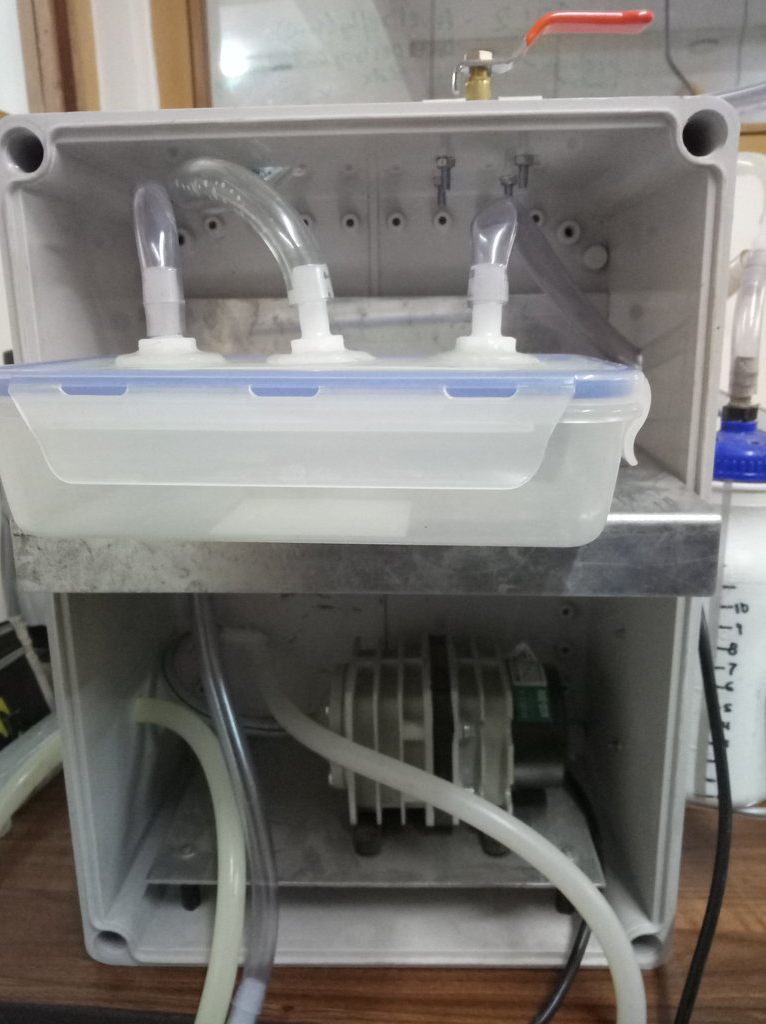
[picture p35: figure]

1.14 | Assembled bubble CPAP | Fig.18

For Internal use only Lattice Innovations FYVE S1 SOP Assembly Instructions Document No – LI/QM/SOP/AI/CPAP Version No. 03 New ___ _________ Revised ___________ Effective Date: Issuing Date: 26-09-2018

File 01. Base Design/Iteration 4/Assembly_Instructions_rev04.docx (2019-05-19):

Assembly instruction for CPAP device

System Diagram


Step 1.1 Prepare the cut outs in the main enclosure

Step | Instruction | Image


1.0 | Make a 40mm X 50mm clearance for cable inlet at any of the side walls of the enclosure. | Fig.0

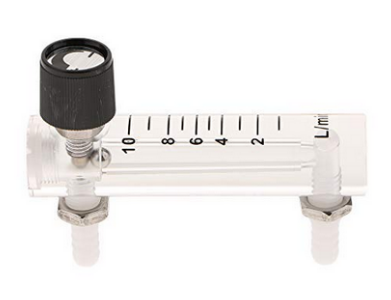
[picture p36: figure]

| Note the type of the flowmeter. make two pairs of 15mm holes 70mm apart for fitting in the flowmeter. | Fig.1

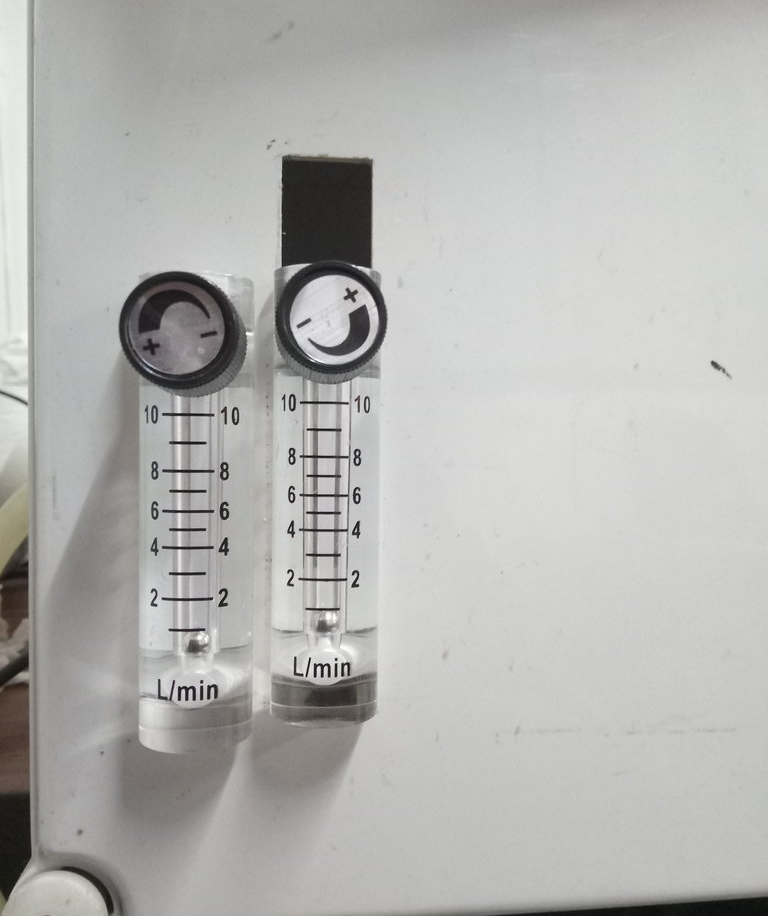
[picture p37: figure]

1.2 | Place it as shown | Fig.2

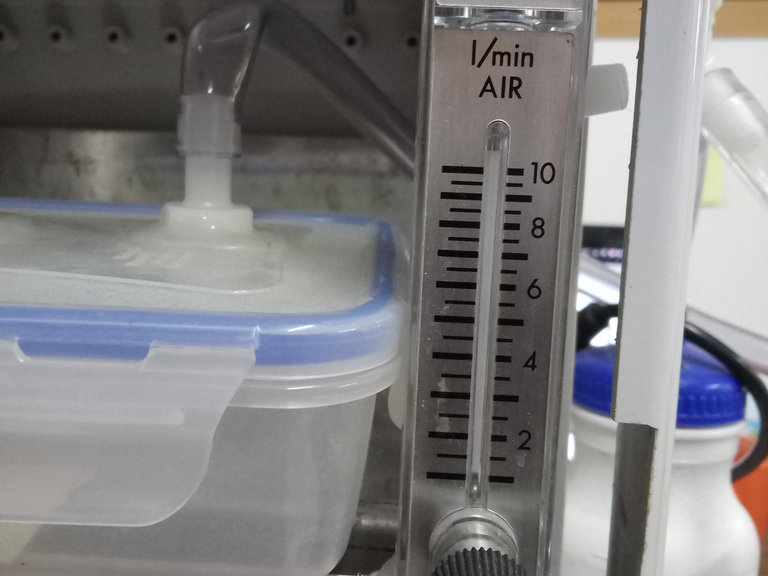
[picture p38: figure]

1.3 | Fix the screws to keep the final output flowmeter in place. | Fig.3


1.4 | Cut two PVC tubes for each flowmeter & connect the elbow connectors to the tubes as shown in the picture. | Fig.4

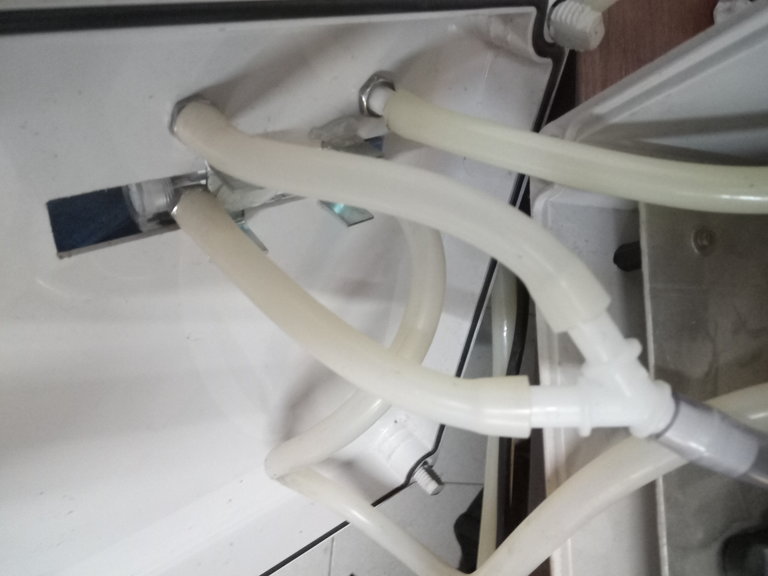
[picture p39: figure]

1.5 | Connect the tubes to the flowmeter. The outputs of both air & oxygen carrying flowmeters are connected through a Y connector. Please refer to the system schematics at the end of the document for more details | Fig.5


1.6 | Drill two holes of 5mm dia & 65mm apart and fix the bottle holder in that location. | Fig.6


1.7 | Prepare the PEEP bottle assembly | Fig.7


| PEEP bottle to be mounted as shown. | Fig.8


| Prepare the base-plate for compressor mounting. Placement of the holes may differ depending on their actual mounting arrangement | Fig.9


1.8 | Assemble the pump & place it in the mounting holes. Make 4 mounting holes for placing the baseplate inside the enclosure. Dimension: 190mm X 90mm | Fig.10


| Connect the compressor outlet to the flowmeter inlet as shown. The outlet of the flowmeter to be connected to the inlet of the humidifier. | Fig.11


1.9 | Preparation of the Humidifier Drill three holes of 12mm dia & 50mm apart and place the threaded elbow connector as shown in the image. Inlet and outlet port of the humidifier & water filling connector. Some masking tape/ glue gun can be applied for achieving better grip & air-tightness. | Fig.12 Fig.13


1.10 | A ball valve is set at the top of the system to fill water in the humidifier. Place the humidifier chamber in the appropriate place. | Fig.14


1.11 | The final placement of compressor & humidifier | Fig.15


1.12 | Drill a hole of 12mm diameter at the center of the cap of the bottle & place the threaded connector & 180mm PVC pipe of 12mm internal diameter. Drill 4 holes of 5mm diameter at the cap of the bottle to insert luer lock tubing. This tube will be connected to a 60ml or 100ml syringe for adding or reducing water to the PEEP bottle. | Fig.16
1.13 | Cut a 115mm tube & place it in between the humidifier chamber outlet & Y connector. Connect the nasal cannula & tubing to the wye connector. | Fig.17


1.14 | Assembled bubble CPAP | Fig.18

For Internal use only Lattice Innovations FYVE S1 SOP Assembly Instructions Document No – LI/QM/SOP/AI/CPAP Version No. 04 New ___ _________ Revised ___________ Effective Date: Issuing Date: 11-11-2018

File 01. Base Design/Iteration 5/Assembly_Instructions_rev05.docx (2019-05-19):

Assembly instruction for CPAP device

System Diagram

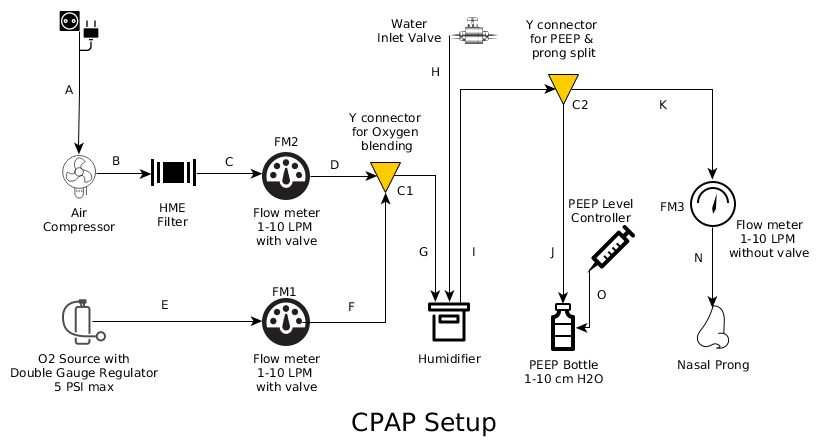
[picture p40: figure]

BOM link: https://docs.google.com/spreadsheets/d/1dIW1Tr6NzaFTdaCL5RmxEFb9l5C3onxBBb0UbcO2Jm4/edit#gid=0

Step 1.1 Prepare the cut outs in the main enclosure

Step | Instruction | Image


1.0 | Make a 40mm X 50mm clearance for cable inlet at any of the side walls of the enclosure. | Fig.0


| Note the type of the flowmeter. make two pairs of 15mm holes 70mm apart for fitting in the flowmeter. | Fig.1


1.2 | Place it as shown (FM1, FM2) | Fig.2


1.3 | Fix the screws on the enclosure front plate to keep the final output flowmeter in place. (FM3) | Fig.3


1.4 | Cut two pair of PVC tubes for each flowmeter & connect the elbow connectors to the tubes as shown in the picture. C-FM2, D-FM2 tubes and E-FM1, F-FM1 tubes assembly. L-Connectors (BOM, sl. no. 2) | Fig.4


1.5 | Connect the tubes to the flowmeter. The outputs of both air & oxygen carrying flowmeters are connected through a Y connector (C1). D-C1 and F-C1 branch, where the other ends of D & F are connected to the FM2 & FM1 outlet . C is connected between FM2 inlet & Air compressor (HME filter is optional) E is connected between O2 valve and FM1 inlet | Fig.5


1.6 | Drill two holes of 5mm dia & 65mm apart and fix the bottle holder in that location. | Fig.6


1.7 | Prepare the PEEP bottle assembly Branches shown: I, C2, J, K | Fig.7


| PEEP bottle to be mounted as shown. | Fig.8


| Prepare the base-plate for compressor mounting. Placement of the holes may differ depending on their actual mounting arrangement | Fig.9


1.8 | Assemble the pump & place it in the mounting holes. Make 4 mounting holes for placing the baseplate inside the enclosure. Dimension: 190mm X 90mm | Fig.10


| Connect the compressor outlet to the flowmeter inlet as shown. The outlet of the flowmeter to be connected to the inlet of the humidifier. Air compressor outlet is directly connected to FM2 inlet via branch C (HME filter & branch B is optional & omitted) | Fig.11


1.9 | Preparation of the Humidifier Drill three holes of 12mm dia & 50mm apart and place the threaded elbow connector as shown in the image. Inlet and outlet port of the humidifier & water filling connector. Some masking tape/ glue gun can be applied for achieving better grip & air-tightness. Parts: Humidifier & connectors for branches G, H, I. Threaded straight connectors. (BOM sl. no. 7) | Fig.12 Fig.13


1.10 | A ball valve is set at the top of the system to fill water in the humidifier. Place the humidifier chamber in the appropriate place. | Fig.14


1.11 | The final placement of compressor & humidifier | Fig.15


1.12 | Drill a hole of 12mm diameter at the center of the cap of the bottle & place the threaded connector & 180mm PVC pipe of 12mm internal diameter. Drill 4 holes of 5mm diameter at the cap of the bottle to insert luer lock tubing. This tube will be connected to a 60ml or 100ml syringe for adding or reducing water to the PEEP bottle. | Fig.16
1.13 | Cut a 115mm tube & place it in between the humidifier chamber outlet & Y connector. Connect the nasal cannula & tubing to the wye connector. | Fig.17

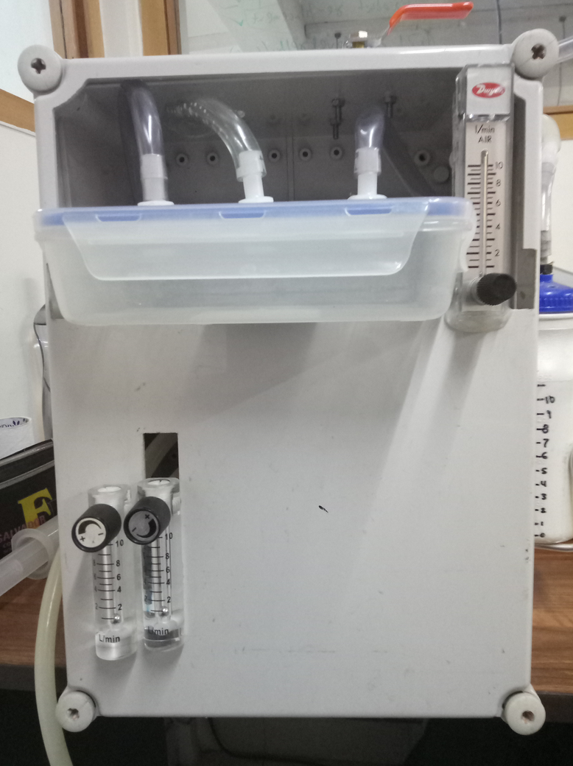
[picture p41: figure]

1.14 | Assembled bubble CPAP | Fig.18

For Internal use only Lattice Innovations FYVE S1 SOP Assembly Instructions Document No – LI/QM/SOP/AI/CPAP Version No. 05 New ___ _________ Revised ___________ Effective Date: Issuing Date: 22-02-2013

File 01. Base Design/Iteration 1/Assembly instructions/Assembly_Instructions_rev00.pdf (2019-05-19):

MODULAR CONTINOUS AIRWAY PRESSURE (MCPAP) DEVICE DEVELOPMENT SOP.

BACKGROUND

Birth Asphyxia, defined as the failure to establish breathing at birth, globally,

## accounts for an estimated 900,000 deaths per year with the biggest proportion in

sub-Saharan Africa.

## Preterm infants commonly suffer from a respiratory/breathing disorder called

### neonatal respiratory distress syndrome (RDS) as their lungs are not yet fully

## developed. The disease is mainly caused by a lack of a slippery substance in the lungs called surfactant that helps the lungs fill with air and keeps the air sacs

from deflating. Surfactant is present when the lungs are fully developed.

## Neonates suffering from RDS often need breathing support until their lungs

start making enough surfactant.

## Continuous positive airway pressure (CPAP) as a therapy for respiratory distress syndrome, is the application of positive pressure to the airways of

spontaneously breathing neonates throughout their respiratory cycle.

## Conventional CPAP is very expensive and hence not affordable in resource constrained settings. We are using locally available low cost plastic bottles and tubing together with a simple pump to develop a low cost modular CPAP device. With the modular CPAP approach, we intend to locally train more

people on how to develop and trouble shoot CPAP devices.

GENERAL STEPS AND PROCEDURES FOR MCPAP DEVICE DEVELOPMENT.

STEP 1: ensure that you have all the materials in place required to make a functional device as listed in the supplies listing.

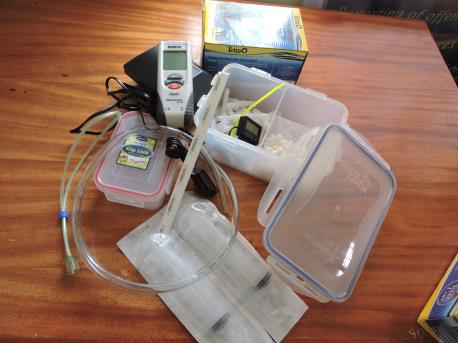
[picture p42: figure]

STEP 2: Drill two holes on the opposite front and back of the big external container. One hole is for the Pump power cable and the other for connection of pump output to tubing.

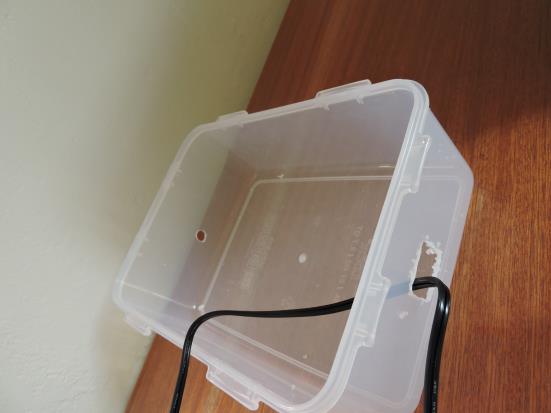
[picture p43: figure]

Step 3: Insert the pump into the container.

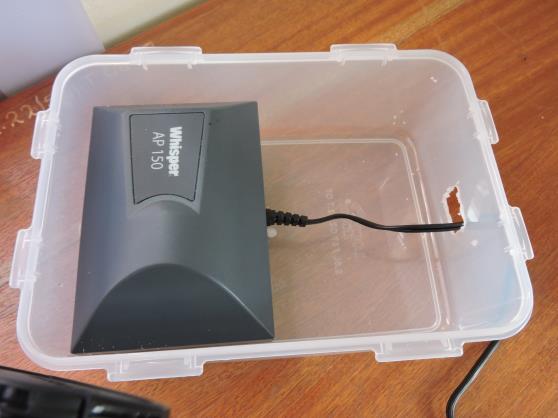
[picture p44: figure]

Step 4: Drill a hole through the container cover enough to insert the PEEP bottle as shown below:

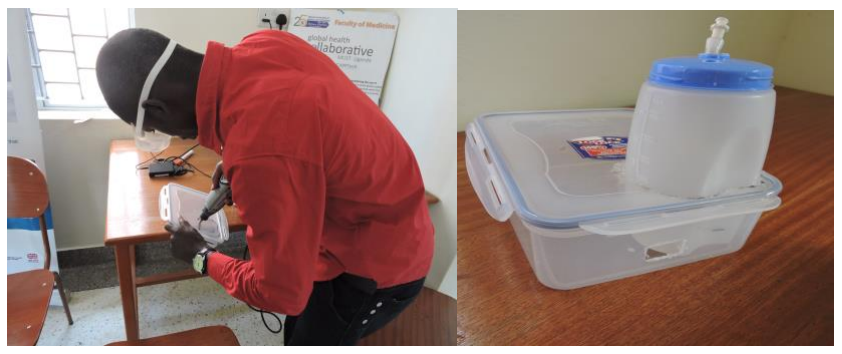
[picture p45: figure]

STEP 5: Drill three holes through the PEEP bottle lead. One hole is for air escape ,second is for connection from Y-junction and the other for depth control using a syringe.

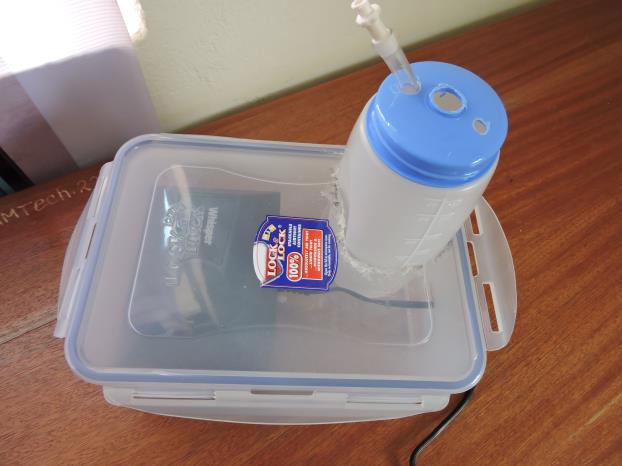
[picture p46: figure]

STEP 6: Using a connector, connect PVC tubing through the peep to the non-corrugated tubing as shown below:

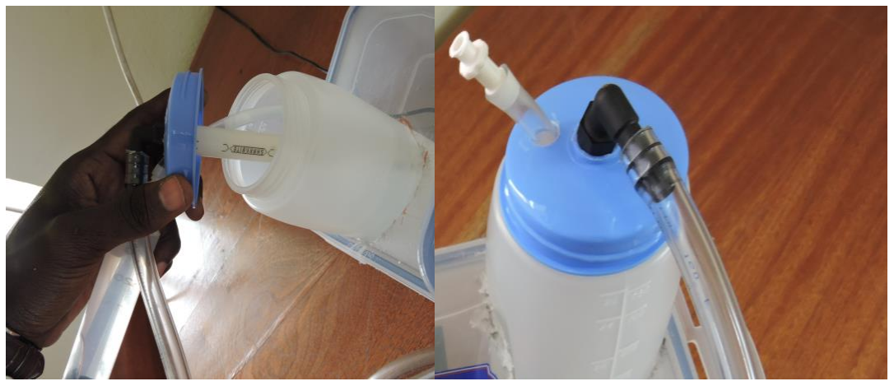
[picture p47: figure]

Step 7: Drill two holes through the small lock container as shown below to create a humidifier. In each of the holes connect an L connector as shown below. Ensure the connectors are to avoid pressure loss.

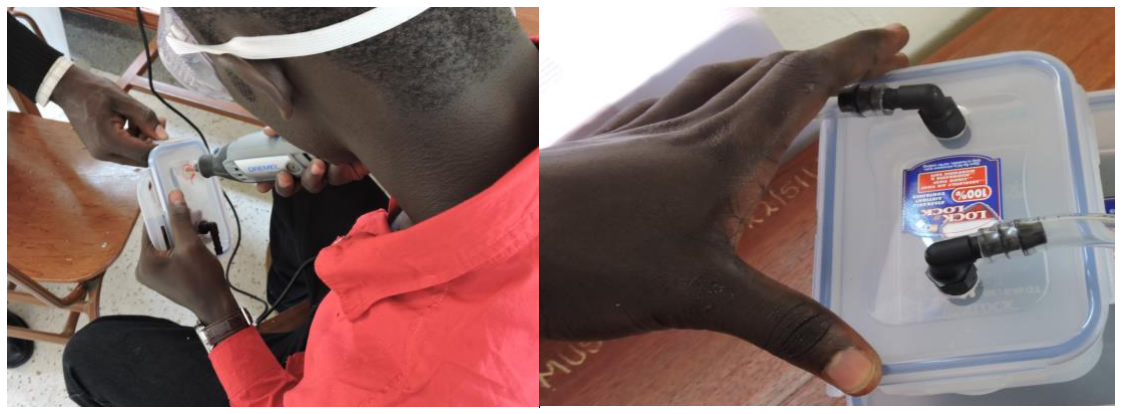
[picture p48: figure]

NOTE: If any leakage is detected, use glue or any other means to seal the leakage.

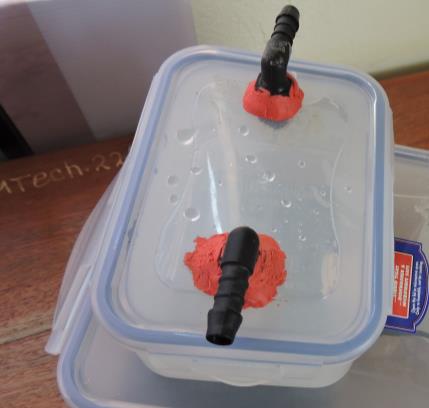
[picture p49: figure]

STEP 9: Using non-corrugated tubing, connect the pump to the humidifier and again humidifier to Y-junction as shown below. Do this with the humidifier at the top of the container containing the pump.

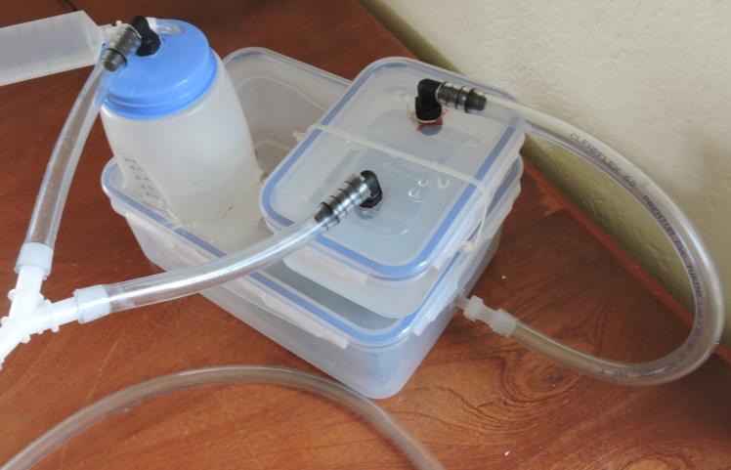
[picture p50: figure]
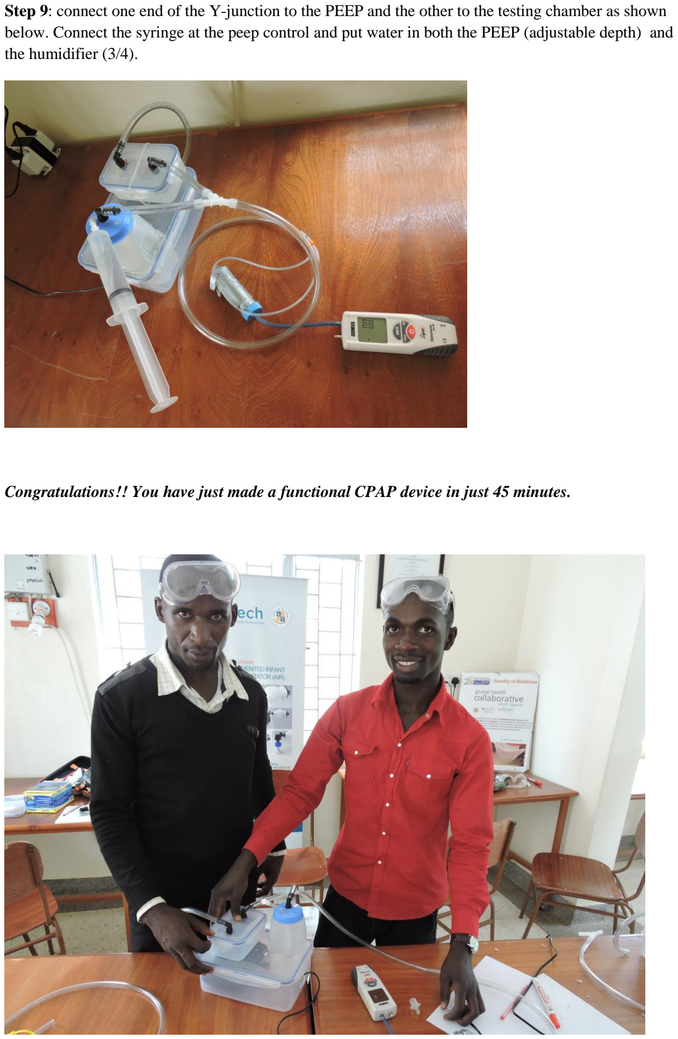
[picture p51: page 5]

Step 9: connect one end of the Y-junction to the PEEP and the other to the testing chamber as shown below. Connect the syringe at the peep control and put water in both the PEEP (adjustable depth) and the humidifier (3/4).

Congratulations!! You have just made a functional CPAP device in just 45 minutes.

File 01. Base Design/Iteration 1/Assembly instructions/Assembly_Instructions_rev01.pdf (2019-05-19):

For Internal use only

Lattice Innovations CPAP SOP Assembly Instructions | Document No – LI/QM/SOP/AI/CPAP
Version No. | 01
New ___ _________ Revised ___________ | Effective Date: 27-06-2017 | Issuing Date: 27-06-2017

## Assembly instruction for CPAP device

### 1. Cut-outs & Assembly Process

Step | Instruction | Image
1.0 | Note the Location of Green Square. Make a cut out of 50mm x 40mm at the back side of the enclosure for the power chord & wall plug clearance. | Fig.0

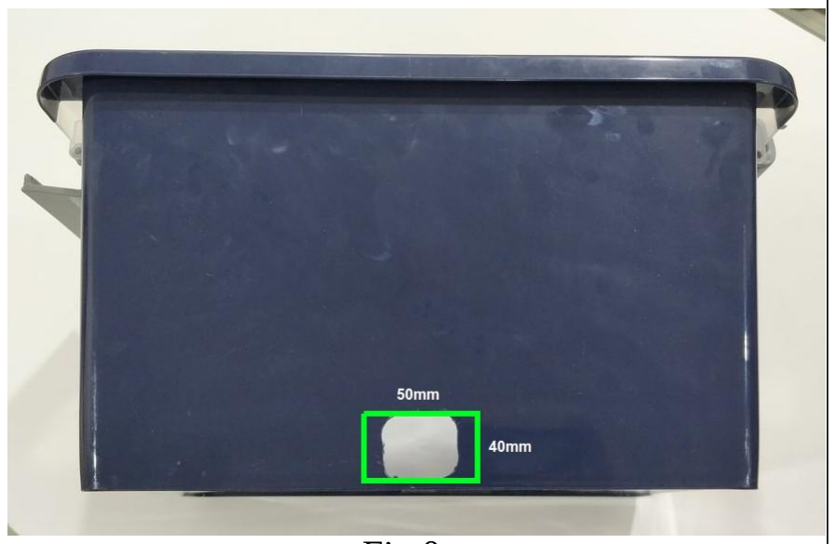
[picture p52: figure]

1.1 | Note the location of Black circles. Install the Flowmeter in this location. | Fig.1

Lattice Innovations CPAP SOP Assembly Instructions | Document No – LI/QM/SOP/AI/CPAP
Version No. | 01
New ___ _________ Revised ___________ | Effective Date: 27-06-2017 | Issuing Date: 27-06-2017
1.2 | Place it as shown | Fig.2


1.3 | Fix the screws to keep the flowmeter in place. | Fig.3

Lattice Innovations CPAP SOP Assembly Instructions | Document No – LI/QM/SOP/AI/CPAP
Version No. | 01
New ___ _________ Revised ___________ | Effective Date: 27-06-2017 | Issuing Date: 27-06-2017
1.4 | Cut two PVC tubes of 250mm & 120mm length & connect the elbow connectors to the tubes as shown in the picture.


Fig.4
1.5 Connect the tubes to the flowmeter. There are no threads built in to the plastic connectors, tighten the elbow connectors carefully & the metal threads will automatically cut the plastic & make an airtight threading.


Fig.5

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


1.6 | Note the location of the Blue circles. Drill two holes of 5mm (4mm suggested) dia & 65mm apart. | Fig.6


1.7 | Mount the bottle holder as shown. | Fig.7

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


Fig.8

Lattice Innovations CPAP SOP Assembly Instructions | Document No – LI/QM/SOP/AI/CPAP
Version No. | 01
New ___ _________ Revised ___________ | Effective Date: 27-06-2017 | Issuing Date: 27-06-2017
1.8 | Assemble the pump & connect it to the bottom tubing of the Flowmeter


Fig.9


Fig.10

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

Fig.11

1.9 Preparation of the Humidifier

Drill two holes of 12mm dia & 110mm apart and place the
threaded elbow connector as shown in the image.


Fig.12

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


| Some masking tape can be applied for achieving better grip & air-tightness. | Fig.13


1.10 | Place the humidifier chamber in the appropriate place & connect the upper tubing from the flow-meter as shown. Place the wye-connector at the RED circle (Fig.6) | Fig.14

Lattice Innovations CPAP SOP Assembly Instructions | Document No – LI/QM/SOP/AI/CPAP
Version No. | 01
New ___ _________ Revised ___________ | Effective Date: 27-06-2017 | Issuing Date: 27-06-2017
1.11 | Cut a 115mm tube & place it in between the humidifier chamber & Y connector


Fig.15
1.12 Drill a hole of 12mm diameter at the center of the cap of the bottle & place the threaded connector & 180mm PVC pipe of 12mm internal diameter.

Drill 4 holes of 5mm diameter at the cap of the bottle to insert luer lock tubing. This tube will be connected to a 60ml or 100ml syringe for adding or reducing water to the PEEP bottle.


Fig.16

Lattice Innovations CPAP SOP Assembly Instructions | Document No – LI/QM/SOP/AI/CPAP
Version No. | 01
New ___ _________ Revised ___________ | Effective Date: 27-06-2017 | Issuing Date: 27-06-2017
1.13 | Place the PEEP bottle in the bottle holder & connect the tubing as shown


Fig.17
1.14 Connect the nasal cannula & tubing to the wye connector.


Fig.18

### 2. Images of the Assembled Product

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


2.1 | Assembled CPAP Top View | Fig.19


2.2 | Assembled CPAP Front View | Fig.20

Lattice Innovations CPAP SOP Assembly Instructions | Document No – LI/QM/SOP/AI/CPAP
Version No. | 01
New ___ _________ Revised ___________ | Effective Date: 27-06-2017 | Issuing Date: 27-06-2017
2.3 | Assembled CPAP
| Back View


Fig.21
2.4 | Assembled CPAP
| Side View


Fig.22

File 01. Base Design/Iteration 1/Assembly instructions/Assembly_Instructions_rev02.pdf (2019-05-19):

For Internal use only; Version No.; New ___ _________ Revised ___________; Effective Date: 23/11/2017; Issuing Date: 23/11/2017; Assembly instruction for CPAP device

Lattice Innovations FYVE S1 SOP Assembly Instructions | Document No – LI/QM/SOP/AI/CPAP
Step 1.1 Prepare the cut outs in the main enclosure

Step; Instruction; Image; Make a cutout of 20mm X; 117mm for Flowmeter mounting; Fig.1

1.0 | Note the Location of Green Square. Make a cut out of 50mm x 40mm at the back side of the enclosure for the power chord & wall plug clearance. | Fig.0

Lattice Innovations FYVE S1 SOP Assembly Instructions | Document No – LI/QM/SOP/AI/CPAP
Version No. | 02
New ___ _________ Revised ___________ | Effective Date: 23/11/2017 | Issuing Date: 23/11/2017
1.2 | Front side of the assembly

Fig.2
1.3 Cut two PVC tubes of 500mm & 180mm length & connect the elbow connectors to the tubes as shown in the picture.

Fig.3

Lattice Innovations FYVE S1 SOP Assembly Instructions | Document No – LI/QM/SOP/AI/CPAP
Version No. | 02
New ___ _________ Revised ___________ | Effective Date: 23/11/2017 | Issuing Date: 23/11/2017
1.4 | Flowmeter position & mounting.

Fig.4
1.5 The threading is already done by inserting & twisting the L connector to the flow-meter inlet & outlets.

Fig.5

Lattice Innovations FYVE S1 SOP Assembly Instructions | Document No – LI/QM/SOP/AI/CPAP
Version No. | 02
New ___ _________ Revised ___________ | Effective Date: 23/11/2017 | Issuing Date: 23/11/2017
1.6 | Now the assembly should look like this.

Fig.6

.7 Cut two holes 30mm apart, as shown, for PEEP bottle mounting.

Fig.7

Lattice Innovations FYVE S1 SOP Assembly Instructions | Document No – LI/QM/SOP/AI/CPAP


Version No. | 02
New ___ _________ Revised ___________ | Effective Date: 23/11/2017 | Issuing Date: 23/11/2017
1.8 | Make four holes in the enclosure & the Base plate.

Base Plate size is 130mm X 220mm

Use 30mm spacer in between the between base of the enclosure & the metallic base plate.

Fig.8

Fig.9

Fig.10

Version No.; New ___ _________ Revised ___________; Effective Date: 23/11/2017; Issuing Date: 23/11/2017; Pump mounted.; Fig.11; Preparation of the Humidifier; Drill two holes of 12mm dia & 110mm apart and place the threaded elbow connector as shown in the image.; Fig.12

Lattice Innovations FYVE S1 SOP Assembly Instructions | Document No – LI/QM/SOP/AI/CPAP

Version No.; New ___ _________ Revised ___________; Effective Date: 23/11/2017; Issuing Date: 23/11/2017; Some masking tape can be applied for achieving better grip & air-tightness.; Fig.13; Prepare the rest for humidifier; chamber; Fig.14

Lattice Innovations FYVE S1 SOP Assembly Instructions | Document No – LI/QM/SOP/AI/CPAP

Version No.; New ___ _________ Revised ___________; Effective Date: 23/11/2017; Issuing Date: 23/11/2017; + 20mm U-clamp to fix the chamber in position; 4mm mounting holes required on either side of the humidifier chamber for placing the clamp; Fig.15; Two seperate chambers for pump; & humidifier placement.; Make a 22mmdia hole for air pipe clearence.; Fig.16

Lattice Innovations FYVE S1 SOP Assembly Instructions | Document No – LI/QM/SOP/AI/CPAP

Lattice Innovations FYVE S1 SOP Assembly Instructions | Document No – LI/QM/SOP/AI/CPAP
Version No. | 02
New ___ _________ Revised ___________ | Effective Date: 23/11/2017 | Issuing Date: 23/11/2017
1.13 | Connect the inlet & outlet of the flowmeter as shown in the picture.

Fig.17
1.14 The outlet tubing from flowmeter to be connected to the humidifier.

Fig.18

Lattice Innovations FYVE S1 SOP Assembly Instructions | Document No – LI/QM/SOP/AI/CPAP
Version No. | 02
New ___ _________ Revised ___________ | Effective Date: 23/11/2017 | Issuing Date: 23/11/2017
1.15 | Connect the nasal cannula & tubing to the wye connector.
| Prepare the peep bottle.

Fig.19
1.16 Bottle Placement.

Fig.20

Version No.; New ___ _________ Revised ___________; Effective Date: 23/11/2017; Issuing Date: 23/11/2017; Assembled CPAP; Front View; Fig.21

Lattice Innovations FYVE S1 SOP Assembly Instructions | Document No – LI/QM/SOP/AI/CPAP

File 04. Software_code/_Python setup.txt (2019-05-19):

Getting Python:
===============
https://www.python.org/downloads/

Getting started with Python:
============================
https://wiki.python.org/moin/BeginnersGuide/Download
https://wiki.python.org/moin/BeginnersGuide

Detailed instructions for OS specific installation guidelines to be added.

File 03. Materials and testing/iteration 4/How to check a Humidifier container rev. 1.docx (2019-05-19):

Title:

Checking airtight humidifier container

Purpose:

To ensure if there are any leakages in the box

Materials required:

1. Humidifier container (In our experiment we have selected ROXX Pure Lock food container, 1ltr. (https://www.amazon.in/Roxx-Rectangular-Container-1-Litre/dp/B007PDU6IQ) ; dimensions: 20 x 12.9 x 6.9 ; L,W,D, all units in cm). Some other optional containers are listed here (https://www.zotero.org/groups/2084057/teamlattice/items/collectionKey/BUNI7D72) as well.
2. Large container (approx or larger than dimensions: 30 x 30 x 15 ; L,W,D, all units in cm)
3. Enough water to fill the large container

Procedure:

Close the container lid properly & entirely dip the container to the bottom of the water filled large container for 5 minutes. Check if any bubble is coming out from the container. After 5 minutes, pull the container out & wash the outside area carefully. Then open the lid & check if any water droplets are left inside. A tissue paper can be used to detect water droplets inside the container.

Results & Conclusion:

If any water droplets are found inside the container it signifies that there is a leakage in the box & it cannot be used in the CPAP device. If no droplets are found, we can go ahead with the box for further setups.

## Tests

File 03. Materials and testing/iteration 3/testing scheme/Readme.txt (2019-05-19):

the attached graphml file can be opened/edited using yed graph editor.

https://www.yworks.com/products/yed/download

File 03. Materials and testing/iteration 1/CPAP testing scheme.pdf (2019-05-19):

Bubble CPAP testing & validation summary | Date: 30-04-2018

Objective:
To observe and understand the relationships between different parameters of the Bubble CPAP system.

Parameters to alter, observe & correlate:
- Flow rate (1lpm to 10 lpm)
- Humidifier water level (1cm to 3cm)
- Humidifier water surface area
- (9.5cm x 15.5mm; 0% to 100%;
to control evaporation rate)
- Pressure level (1cm to 11cm of H2O)

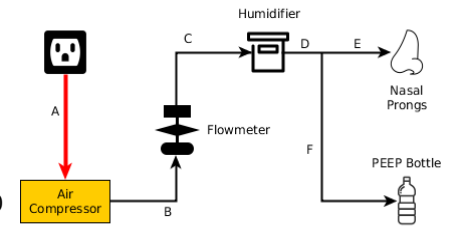
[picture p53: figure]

- Temperature (ambient & compressed Air)
- Humidity (ambient & compressed Air)

Fig. 1: System overview
Experimental setup:
There are four major parts of this experimental setup.
i) Sensors Selection.
ii) Data acquisition.
iii) Data logging
iv) Plots, graphs & data analysis.

Sensors & measuring devices:
A number of sensors are deployed along the breathing circuit for measuring different parameters.

Gas Sensors: (For detecting level of concentration of the gases)
MQ-2: useful for detecting H2, LPG, CH4, CO, Alcohol, Propane.
MQ-5: useful for detecting LPG, Natural gas, Town gas.
MQ-135: useful for detecting NH3, C6H6, smoke, CO2.

Temperature & Humidity Sensors: (For collecting both ambient & relative data) DHT11: 16 bit resolution temperature & relative humidity sensor.

Pressure Measurement: (For detecting leakage & measuring pressure)
PM-6205: HTC Instrument Digital Manometer.

Flow Measurement:
Dwyer Rate-master flow-meter.

Data Acquisition:
Data is collected using an embedded microcontroller attached to the sensors. The interval between each data point is 3 seconds.

Data logging:
Since the space provided in the internal EEPROM of the controller is very small, we have logged the data into spreadsheet using serial programming & python.

Plots, Graphs & data analysis:
Visualizing the data trend, cross-correlation between different parameters such as flow-rate vs humidity or flow-rate vs pressure.

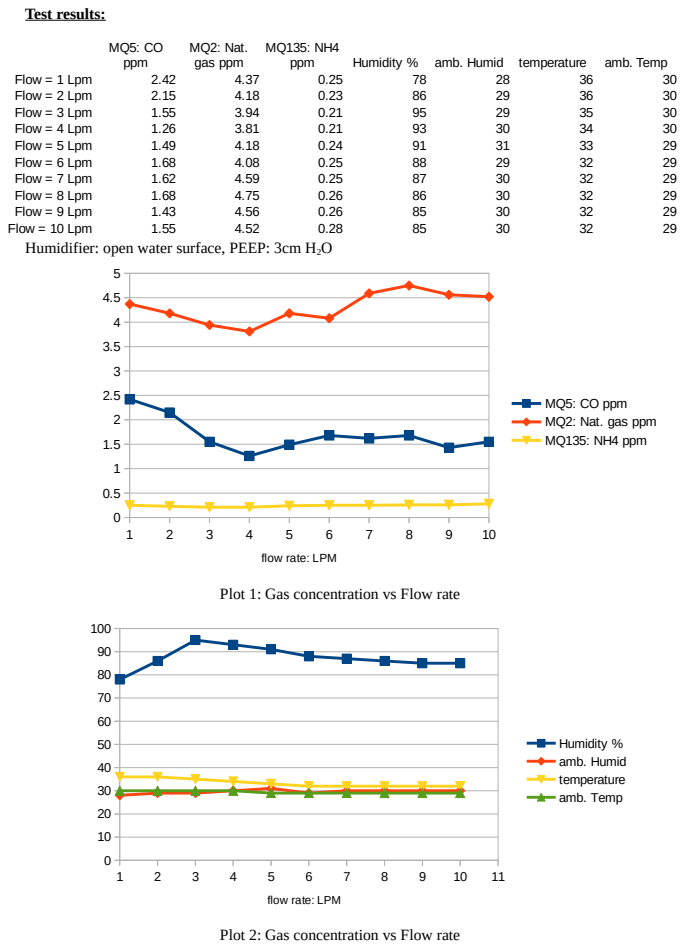
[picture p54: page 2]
Test results:; Humidity % amb. Humid temperature; amb. Temp; Flow = 1 Lpm; Flow = 2 Lpm; Flow = 3 Lpm; Flow = 4 Lpm; Flow = 5 Lpm; Flow = 6 Lpm; Flow = 7 Lpm; Flow = 8 Lpm; Flow = 9 Lpm; Flow = 10 Lpm; MQ5: CO ppm; MQ2: Nat. gas ppm; MQ135: NH4 ppm; Humidity % amb. Humid temperature amb. Temp

Humidifier: open water surface, PEEP: 3cm H2O

MQ5: CO ppm
MQ2: Nat. gas ppm
MQ135: NH4 ppm

flow rate: LPM
Plot 1: Gas concentration vs Flow rate

Plot 2: Gas concentration vs Flow rate

Test setup:

In this experiment we have considered three major parameters i.e. Pressure, Volume/ rate of flow & Humidity level & tried to find out the correlation between them. Ambient temperature & humidity measurement has also been done in order to calibrate the gas sensor.

The CPAP device is set up as shown in Fig 1. Air compressor is connected to a 220 V wall socket. The Flow meter is directly connected to the compressor outlet.

Air flow through the breathing circuit is controlled
by a pin valve provided in the flow meter that can
deliver flow rates ranging from 1LPM to 10 LPM.

The next component in the breathing circuit is the Humidifier. Since evaporation occurs only on the surface of a liquid, small templates are created using PP sheets that covers certain areas of the water surface. Internal area of the humidifier is approx
9.5cm X 15.5 cm. We have found that the rate of
change of humidity is directly proportional to the

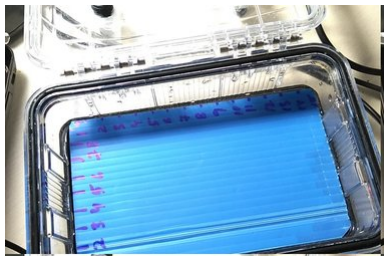
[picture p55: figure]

open surface of the water. | Fig. 2: Humidifier

3 pairs of humidity, temperature and gas sensors are
deployed at the opening of the nasal prongs to detect
the level of heat, moisture & gas concentration at
both the ambient & test conditions. Ambient levels

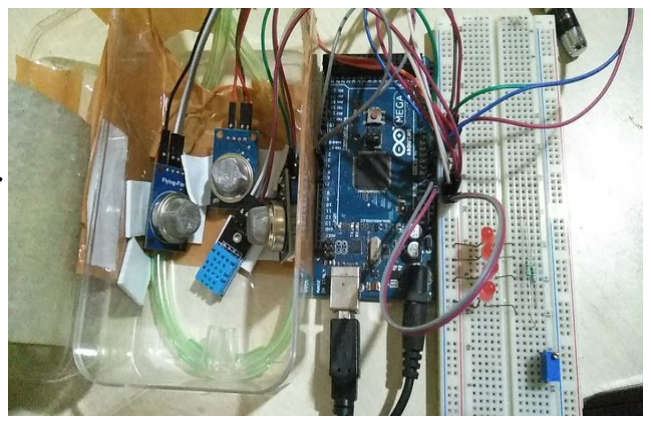
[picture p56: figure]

are required to calibrate the sensitivity of the sensors.

PEEP bottle has been marked with 0cm to 11cm H2O pressure levels. In this experimental setup the PEEP level is also variable & at each level, the same
experiment to be carried out to understand the
relation between humidity & gas concentration at
different pressure levels. | Fig. 3: Gas, temperature & humidity sensor

The data has been collected using a microcontroller
platform & sent to the PC using USB
communication. A simple python script is written to
automatically log it into a spreadsheet.

Analogue to Digital conversion values are used to
calculate the PPM concentration of the gases.

The following parameters are measured during the

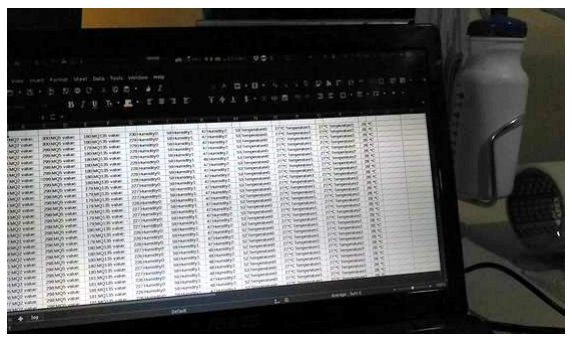
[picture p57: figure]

testing process. | Fig. 4: Data logging using python

Flow = 7lpm
Duration: 25 min Humidifier water height = 1cm Humidifier surface covered area = 9.5x15.5 sq.cm
PEEP = 2cm

sl. no.
0 | MQ2 value: 363 | MQ5 value: 197 | MQ135 value: 316 | Humidity0: 44 | Humidity1: 42 | Humidity2: 52 | Temperature0: 30 | *C Temperature1: 30 | *C Temperature2: 34 | *C
1 | MQ2 value: 365 | MQ5 value: 197 | MQ135 value: 316 | Humidity0: 44 | Humidity1: 42 | Humidity2: 52 | Temperature0: 30 | *C Temperature1: 30 | *C Temperature2: 34 | *C
2 | MQ2 value: 364 | MQ5 value: 197 | MQ135 value: 316 | Humidity0: 44 | Humidity1: 42 | Humidity2: 52 | Temperature0: 30 | *C Temperature1: 30 | *C Temperature2: 34 | *C
3 | MQ2 value: 364 | MQ5 value: 197 | MQ135 value: 317 | Humidity0: 44 | Humidity1: 42 | Humidity2: 52 | Temperature0: 30 | *C Temperature1: 30 | *C Temperature2: 34 | *C

Observations:

sl. no. | Observations | Remarks
1. Electrical Properties of the compressor is in | line with the specifications provided by the manufacturer. It has an issue of making excessive vibration during the run. | Rubber pads are provided at the base of the motor to absorb the vibration. Mounting screws and internal assembly is not affected by continuous 8 hours run for 5 days. The Noise and vibration is not affecting the working of the CPAP device.
| | No significant level of harmful gases are found during the run.
2. Water column height & area is altered to | understand the relation between evaporation & humidification levels. | Humidification is directly proportional to the area exposed to air inside the humidifier.
| | Ambient humidity is also taken under consideration & the value is measured using separate humidity sensor during the test run.
3. Air compressor dissipates heat during the | run. 3 temperature sensors are deployed; 2 for ambient & 1 at the outlet of the nasal prong to understand the rise of air temperature through the breathing circuit | A maximum difference of 6 degree is observed during the testing. (Ambient: 30*C, Breathing Ckt: 36*C)

Scope:

Leakage detection in the breathing circuit, pressure difference at different points of the circuit etc. to be verified.

A more robust & calibrated gas sensing technique can be adopted to identify the exact gases that are causing the mild foul smell in the breathing circuit.

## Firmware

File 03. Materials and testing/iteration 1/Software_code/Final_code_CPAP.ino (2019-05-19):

#define DHTTYPE DHT11   // DHT 11         
#include "DHT.h"

#define DHTPIN 2     // what digital pin we're connected to
#define DHTPIN1 3
#define DHTPIN2 4 
DHT dht(DHTPIN, DHTTYPE);
DHT dht1(DHTPIN1, DHTTYPE);
DHT dht2(DHTPIN2, DHTTYPE);

void MQ5calculation();   
float Rs5 = 0.0 ;
float RS5_air = 0.0; 
float Ro5 = 0.0;
float sensor_volt = 0.0;
float sensor_volt1 = 0.0;
float sensor_volt2 = 0.0;
float sensorValue=0;
float sensorValue1=0;
float sensorValue2=0;

void MQ2calculation();
float Rs2 = 0.0 ;
float RS2_air = 0.0; 
float Ro2 = 0.0;

void MQ135calculation();
float Rs135 = 0.0 ;
float RS135_air = 0.0; 
float Ro135 = 0.0;

void setup() {
 Serial.begin(115200);
  Serial.print("\n");
  dht.begin();
  dht1.begin();
  dht2.begin();
  voltcalc();
}
void voltcalc()
{
Serial.print(" Calibrating.......");
for(int x = 0 ; x < 32000 ; x++)
    {
        sensorValue = sensorValue + analogRead(A0);
        sensorValue1 = sensorValue1 + analogRead(A1);
        sensorValue2 = sensorValue2 + analogRead(A2);
        
    }
    sensorValue = (sensorValue/32000.0);
    sensorValue1 = (sensorValue1/32000.0);
     sensorValue2 = (sensorValue2/32000.0);

    sensor_volt = (sensorValue/1024)*5.0;
    sensor_volt1 = (sensorValue1/1024)*5.0;
    sensor_volt2 = (sensorValue2/1024)*5.0;

//    MQ5 Calculation
//---------------------------------------------------------------------------------------------       
    Rs5= (5.0-sensor_volt)/sensor_volt; // omit *RL
    Ro5 = Rs5/6.5; // The ratio of RS/R0 is 9.8 in a clear air from Graph (Found using WebPlotDigitizer)
//-------------------------------------------------------------------------------------------------

// MQ2 Calculation
//--------------------------------------------------------------------------------------------
   Rs2= (5.0-sensor_volt1)/sensor_volt1; // omit *RL
   Ro2 = Rs2/9.83; // The ratio of RS/R0 is 9.8 in a clear air from Graph (Found using WebPlotDigitizer)
//---------------------------------------------------------------------------------------------

//  MQ135 Calculation
//--------------------------------------------------------------------------------------------------
 Rs135= (5.0-sensor_volt2)/sensor_volt2; // omit *RL
 Ro135 = Rs135/3.6; // The ratio of RS/R0 is 9.8 in a clear air from Graph (Found using WebPlotDigitizer)

//--------------------------------------------------------------------------------------------------

    delay(100);
}

void loop() 
{
 float h = dht.readHumidity();
  // Read temperature as Celsius (the default)
  float t = dht.readTemperature();
  // Read temperature as Fahrenheit (isFahrenheit = true)
  float f = dht.readTemperature(true);

  float h1 = dht1.readHumidity();
  // Read temperature as Celsius (the default)
  float t1 = dht1.readTemperature();
  // Read temperature as Fahrenheit (isFahrenheit = true)
  float f1 = dht1.readTemperature(true);


  float h2 = dht2.readHumidity();
  // Read temperature as Celsius (the default)
  float t2 = dht2.readTemperature();
  // Read temperature as Fahrenheit (isFahrenheit = true)
  float f2 = dht2.readTemperature(true);
  // Check if any reads failed and exit early (to try again).

  // Compute heat index in Fahrenheit (the default)
  float hif = dht.computeHeatIndex(f, h);
  // Compute heat index in Celsius (isFahreheit = false)
  float hic = dht.computeHeatIndex(t, h, false);

    float hif1 = dht1.computeHeatIndex(f, h1);
  // Compute heat index in Celsius (isFahreheit = false)
  float hic1 = dht1.computeHeatIndex(t, h1, false);

  float hif2 = dht.computeHeatIndex(f, h2);
  // Compute heat index in Celsius (isFahreheit = false)
  float hic2 = dht.computeHeatIndex(t, h2, false);
  
  Serial.print("Humidity: ");
  Serial.print(" %\t");
  Serial.print(h);
  Serial.print(" %\t");
  Serial.print("Temperature: ");
  Serial.print(" %\t");
  Serial.print(t);
  Serial.print(" %\t");
  Serial.println(" *C ");

   Serial.print("Humidity1: ");
  Serial.print(" %\t");
  Serial.print(h1);
  Serial.print(" %\t");
  Serial.print("Temperature1: ");
  Serial.print(" %\t");
  Serial.print(t1);
  Serial.print(" %\t");
  Serial.println(" *C ");

   Serial.print("Humidity2: ");
  Serial.print(" %\t");
  Serial.print(h2);
  Serial.print(" %\t");
  Serial.print("Temperature2: ");
  Serial.print(" %\t");
  Serial.print(t2);
  Serial.print(" %\t");
  Serial.println(" *C ");
MQ5calculation();
MQ2calculation();
MQ135calculation();

 delay(100);
}
void MQ5calculation()
{
float MQ5volt;
float ratio;
float Rs5_air;

int MQ5value = analogRead(A0);
MQ5volt= (float)MQ5value / 1024*5.0;
Rs5_air = (5.0-MQ5volt)/MQ5volt;
ratio = Rs5_air/Ro5;
 float COcurve []  = { 2.3, 0.60, -0.13 } ; 
 float Alcurve [] = {2.3, 0.54, -0.2} ;   
 float Hcurve [] = {2.3, 0.25, -0.25};
 float Hppm =  pow(10,( ((log(ratio)-Hcurve[1])/Hcurve[2])+ Hcurve[0]));
 float COppm = pow(10,( ((log(ratio)-COcurve[1])/COcurve[2]) + COcurve[0]));
 float Alppm = pow(10,( ((log(ratio)-Alcurve[1])/Alcurve[2])+ Alcurve[0]));
 Serial.print("    Carbon Monoxide ppm:\t");
 Serial.print(COppm);
 Serial.print("    Alcohol Content ppm: \t");
 Serial.print(Alppm);
 Serial.print("    Hydrogen Content ppm: ");
 Serial.println(Hppm);
}

void MQ2calculation()
{
float MQ2volt;
float ratio1;
float Rs2_air;

int MQ2value = analogRead(A1);
MQ2volt= (float)MQ2value / 1024*5.0;
Rs2_air = (5.0-MQ2volt)/MQ2volt;
ratio1 = Rs2_air/Ro2;
 float COcurve []  = { 2.3, 0.7, -0.31 } ; 
 float Scurve [] = {2.3, 0.54, -0.44} ;   
 float LPcurve [] = {2.3, 0.23, -0.47};
 float Sppm =  pow(10,( ((log(ratio1)-Scurve[1])/Scurve[2])+ Scurve[0]));
 float COppm = pow(10,( ((log(ratio1)-COcurve[1])/COcurve[2]) + COcurve[0]));
 float LPppm = pow(10,( ((log(ratio1)-LPcurve[1])/LPcurve[2])+ LPcurve[0]));
 Serial.print("    Carbon MonoxideMQ2 ppm:\t");
 Serial.print(COppm);
 Serial.print("    Smoke ContentMQ2 ppm: \t");
 Serial.print(Sppm);
 Serial.print("    LPG ContentMQ2 ppm: ");
 Serial.println(LPppm);
}

void MQ135calculation()
{
float MQ135volt;
float ratio2;
float Rs135_air;

int MQ135value = analogRead(A2);
MQ135volt= (float)MQ135value / 1024*5.0;
Rs135_air = (5.0-MQ135volt)/MQ135volt;
ratio2 = Rs135_air/Ro135;
 float COcurve []  = { 1, 0.45, -0.23 } ; 
 float NH4curve [] = {1, 0.41, -0.4} ;   
 float C6H6curve [] = {1, 0.18, -0.31};
 float NH4ppm =  pow(10,( ((log(ratio2)-NH4curve[1])/NH4curve[2])+ NH4curve[0]));
 float COppm = pow(10,( ((log(ratio2)-COcurve[1])/COcurve[2]) + COcurve[0]));
 float C6H6ppm = pow(10,( ((log(ratio2)-C6H6curve[1])/C6H6curve[2])+ C6H6curve[0]));
 Serial.print("    Carbon MonoxideMQ135 ppm:\t");
 Serial.print(COppm);
 Serial.print("    NH4 ContentMQ135 ppm: \t");
 Serial.print(NH4ppm);
 Serial.print("    Acetone/Benzene ContentMQ135 ppm: ");
 Serial.println(C6H6ppm);
}

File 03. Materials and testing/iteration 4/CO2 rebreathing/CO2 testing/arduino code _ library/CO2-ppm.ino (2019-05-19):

// The load resistance on the board
#define RLOAD 22.0
// Calibration resistance at atmospheric CO2 level
#define RZERO 879.13 
#include "MQ135.h" 
MQ135 gasSensor = MQ135(A6); 
int val; 
int sensorPin = A6; 
int sensorValue = 0; 
int sl=0;
void setup() { 
  Serial.begin(9600);
  pinMode(sensorPin, INPUT); 
} 

void loop() { 
  Serial.print (sl);
  val = analogRead(A6); 
  Serial.print ("raw = "); 
  Serial.print (" \t");
  Serial.print (val);
  Serial.print (" \t");
  float zero = gasSensor.getRZero(); 
  Serial.print ("rzero: "); 
  Serial.print (" \t");
  Serial.print (zero); 
  Serial.print (" \t");
  float ppm = 0;
  for (int i=0; i<5000; i++){
    ppm = ppm + gasSensor.getPPM();
  }
  ppm = ppm/5000;
  Serial.print ("CO2 ppm: "); 
  Serial.print (" \t");
  Serial.print (ppm); 
  Serial.print (" \t");
  Serial.println (); 
  sl++;
  delay(100); 
}
